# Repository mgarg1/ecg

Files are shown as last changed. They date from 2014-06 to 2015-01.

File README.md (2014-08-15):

ECG
===

An electrocardiograph prototype for the Remote Neonatal Monitoring and Intervention Project.

Dependencies
------------

- Python 2.7
- Arduino >= 1.5.6-r2 (for Arduino Due)
- stream-plot (source included, but streamplot's dependencies need to be met) - https://github.com/s-gv/stream-plot
- MATLAB / Octave if you want to run simulations
- TI SmartRF Flash Programmer
- IAR 8051 >= 8.30 (only if you want to re-compile the source code for CC2540)
- TI CCDebugger (for programming CC2540)

How-to-use
----------

Wired ECG with Arduino:

- Build the circuit in `schematics/ecg_arduino.png`. A USB to UART converter such as FT232 or CP2102 may be used.
- Program the Arduino with the source in `ecg_arduino/ecg_arduino.ino`.
- Goto `ecg_visualizer_arduino_PC/` and run `python visualizer.py`. If the serial port name is incorrect, edit `visualizer.py`.
- Press the hi-z electrodes across the heart and press the RLD electrode to the leg or forehead. Alternatively, the outer ring of one of the hi-z electrodes can be connected to the RLD electrode. For more details, see the technical report in `report/ecg_tech_report.pdf`. You should now see an ECG signal on the PC display.
- Note that a laptop (with the power cord removed) must be used to power the Arduino. Preferably, keep the laptop on your lap. Interference will be much worse if a mains powered desktop is used; the interference may be so strong as to saturate the amplifiers leading to no useful ECG signal at all.

Wireless ECG with Bluetooth Low Energy (BLE using CC2540):

- Build the circuit in `schematics/ecg_CC2540.png`. A more complete schematic is in `schematics/ecg_CC2540_full.png`. Program the CC2540 in the circuit with the hex file `ecg_CC2540/hexfiles/SimpleBLEPeripheral.hex`.
- Connect the CC2540 USB dongle to a PC (either a laptop or a mains powered desktop will do). Program the CC2540 USB dongle with the hex file `ecg_CC2540/hexfiles/CC2540_USBdongle_HostTestRelease_All.hex`.
- Goto `ecg_visualizer_ble_PC/` and run `python visualizer.py`. If the serial port name is incorrect, edit `visualizer.py`.
- Press the hi-z electrodes across the heart and press the RLD electrode to the leg or forehead. Alternatively, the outer ring of one of the hi-z electrodes can be connected to the RLD electrode. For more details, see the technical report in `report/ecg_tech_report.pdf`. You should now see an ECG signal on the PC display. A sample recording may be found [here](https://github.com/s-gv/ecg/blob/master/data/ble_single_battery_LP5907_psuedo2_RLD/screenshots/screenshot0.png).
- Note that the CC2540, which is gathering ECG data and transmitting wirelessly, has to be powered by a battery (ex: CR2032 coin cell). If a mains power source is used, interference will be much worse.

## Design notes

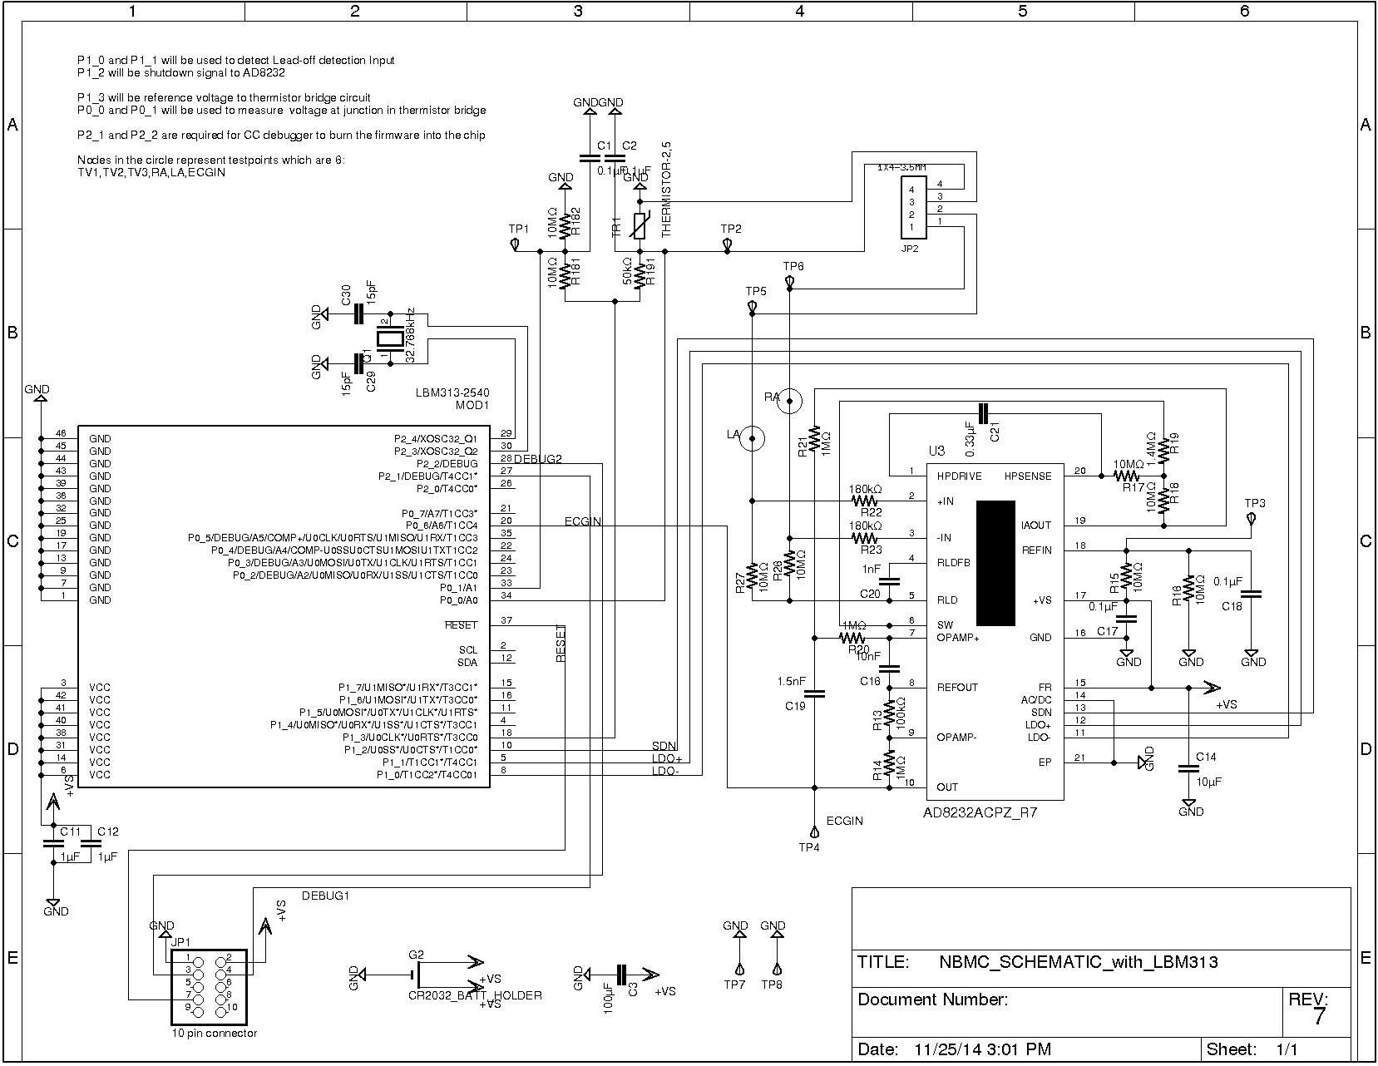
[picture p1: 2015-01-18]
ecg_schematic/LBM313/schematic_black.png

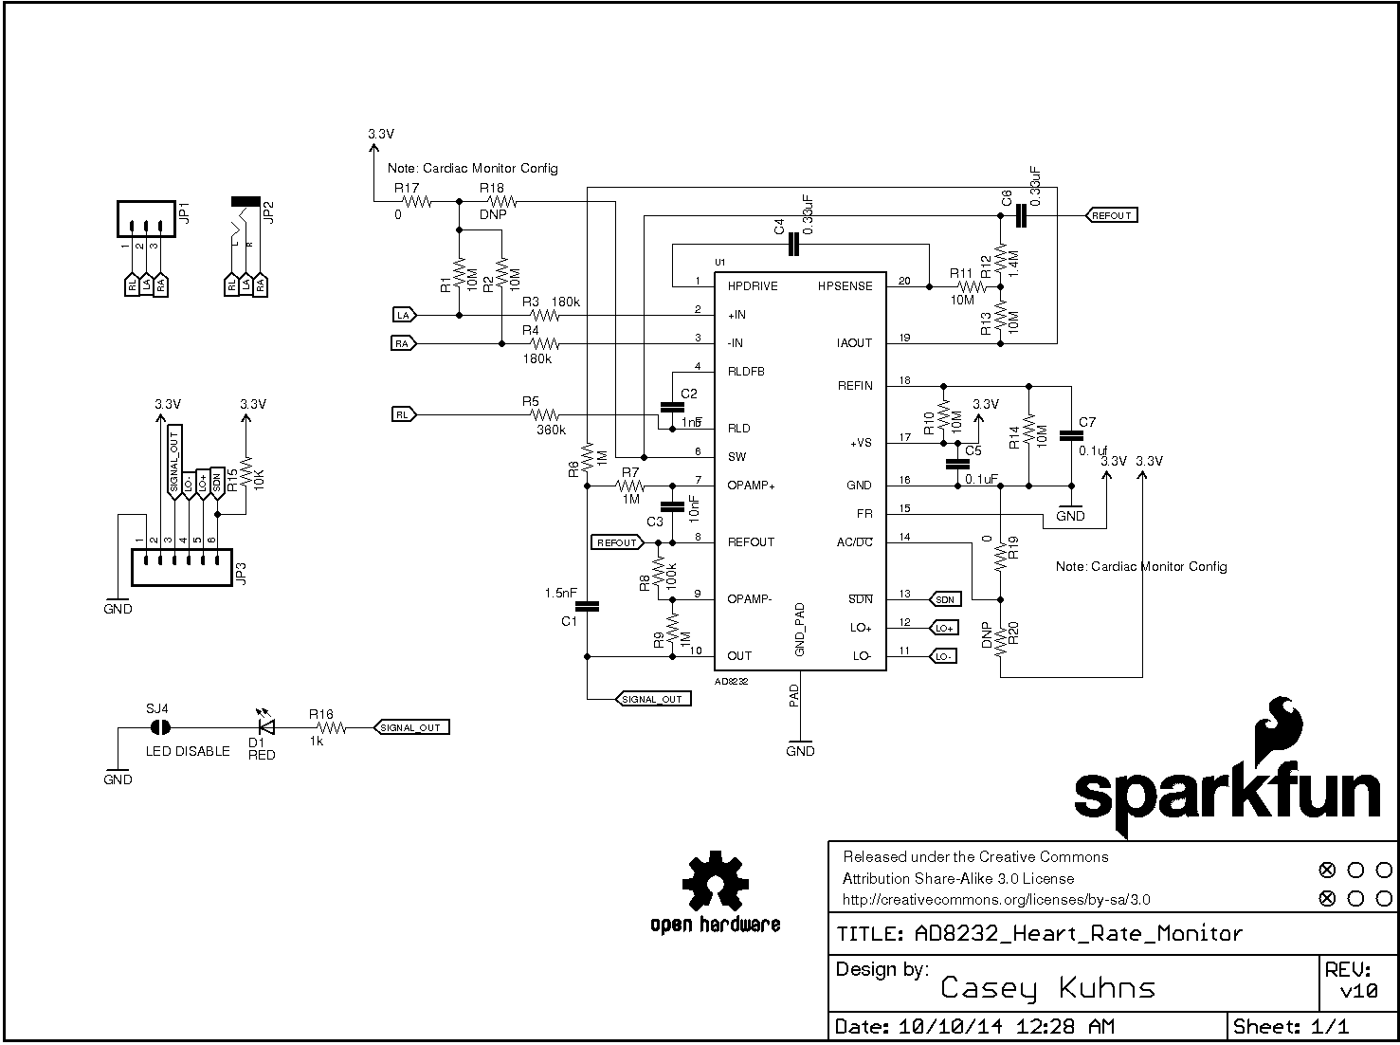
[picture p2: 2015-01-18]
ecg_schematic/Sparkfun_8232/sparkfun_schematic.png

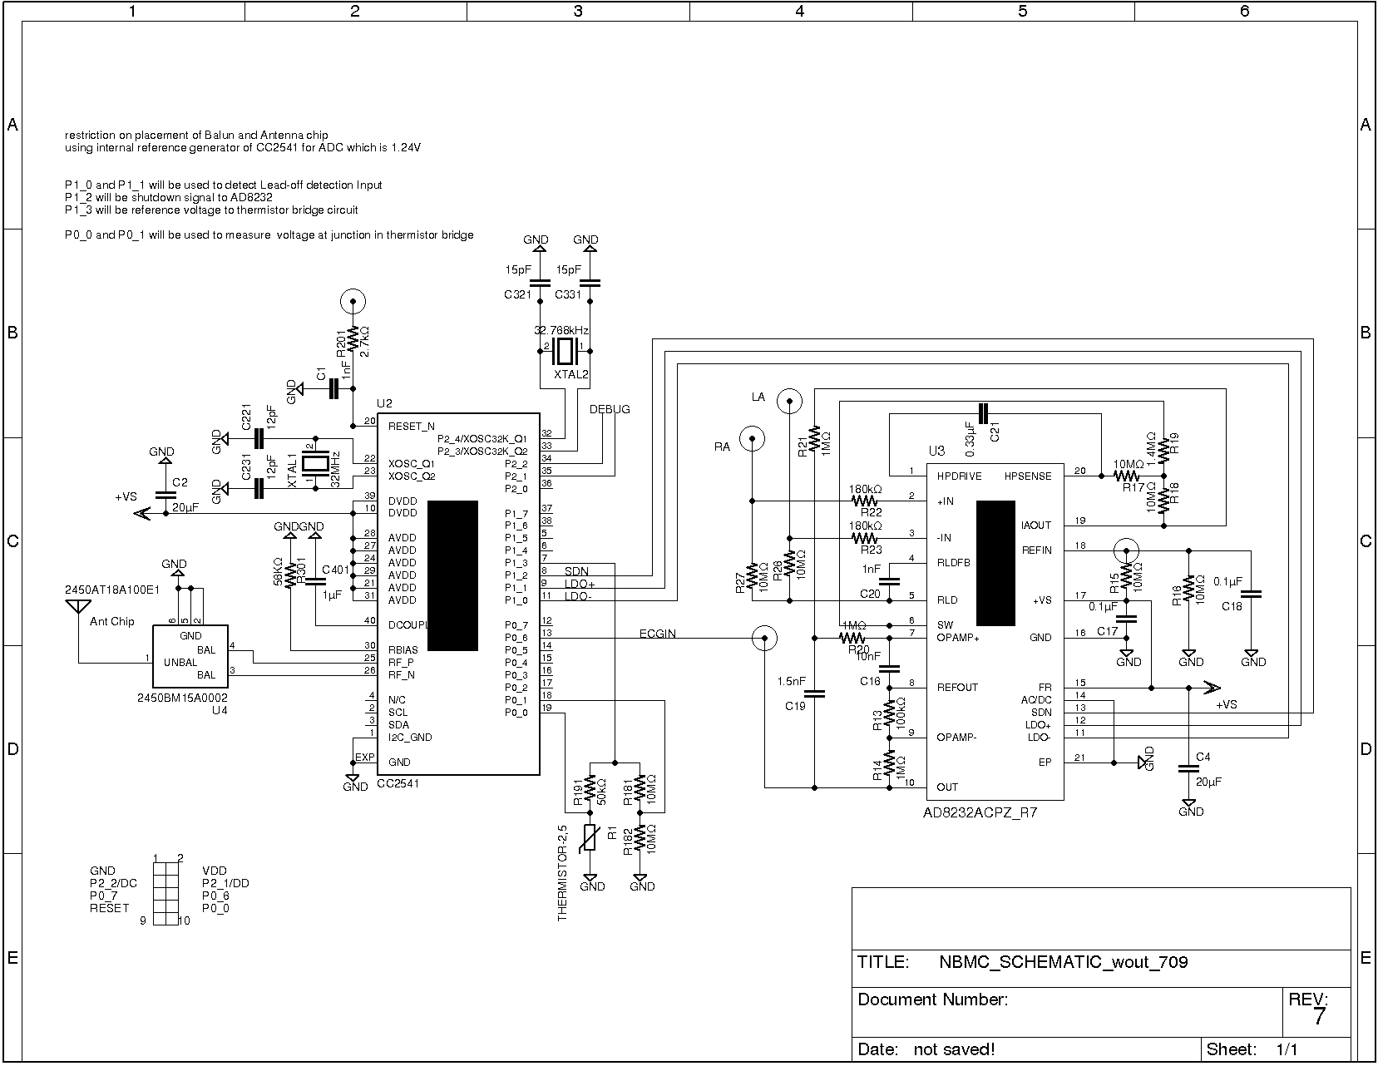
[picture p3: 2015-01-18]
ecg_schematic/NBMC_balun_chip/NBMC_schematic_8.png

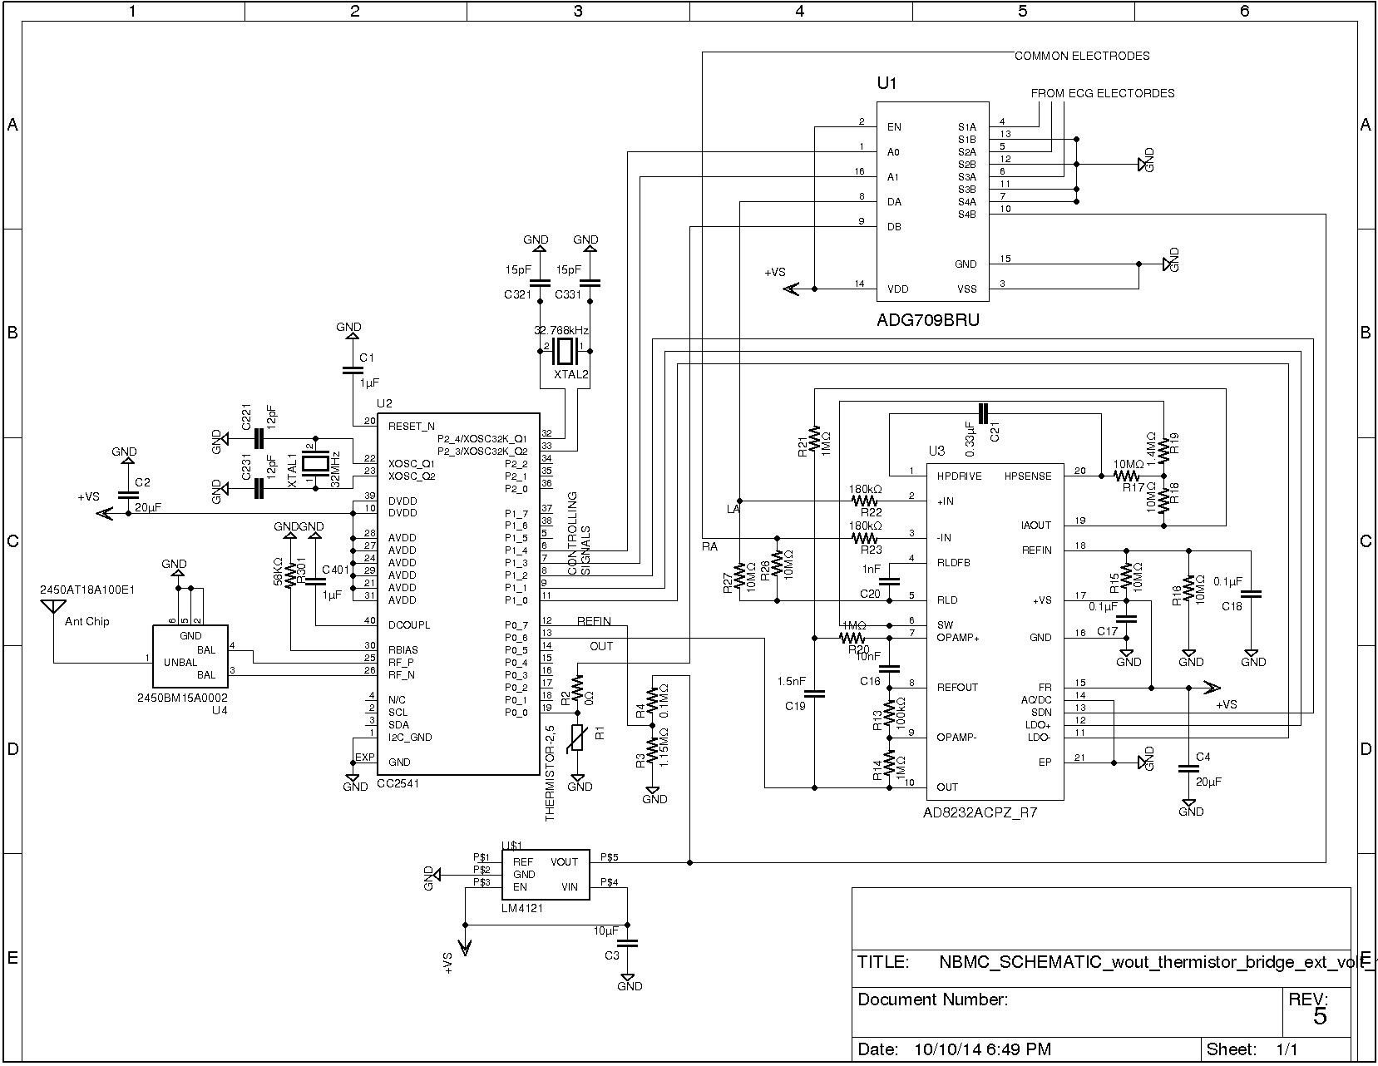
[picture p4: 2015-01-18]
ecg_schematic/NBMC_balun_chip/NBMC_Schematic_5.png

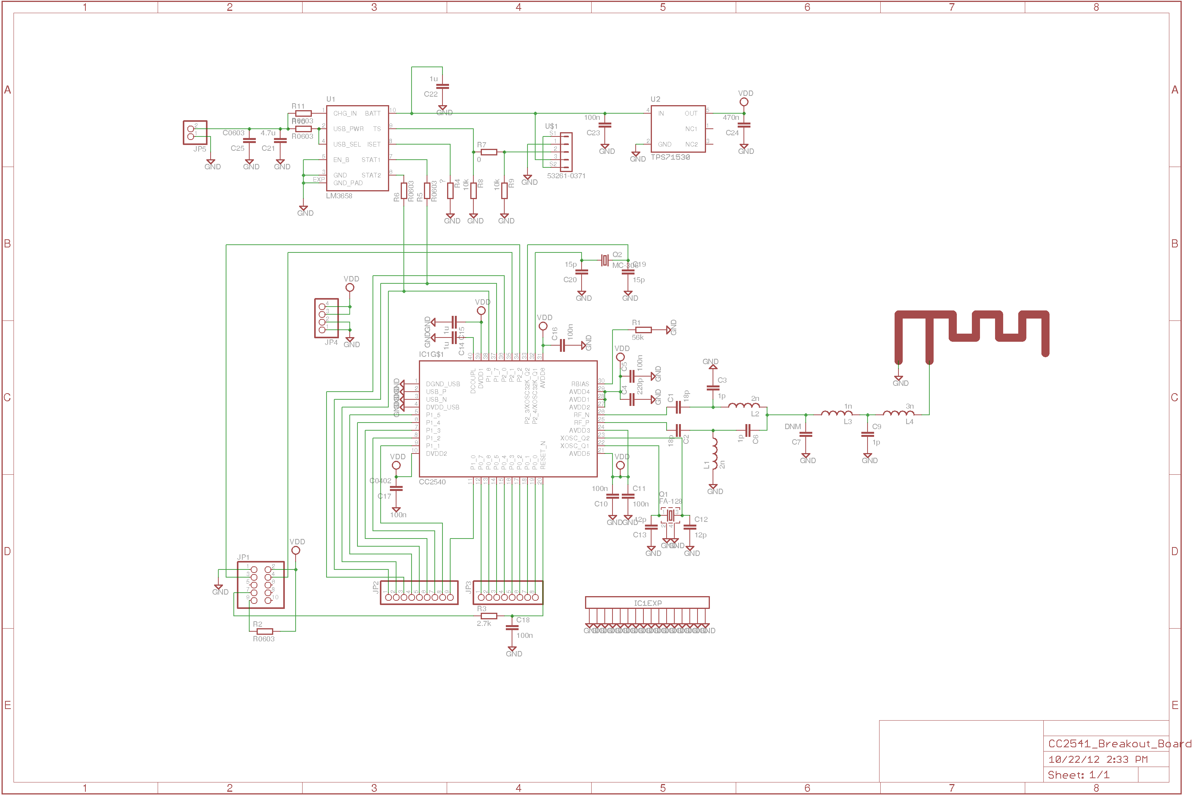
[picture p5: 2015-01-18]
ecg_schematic/CC2541_Breakout_Board_Eagle_files/CC2541_breakout.png

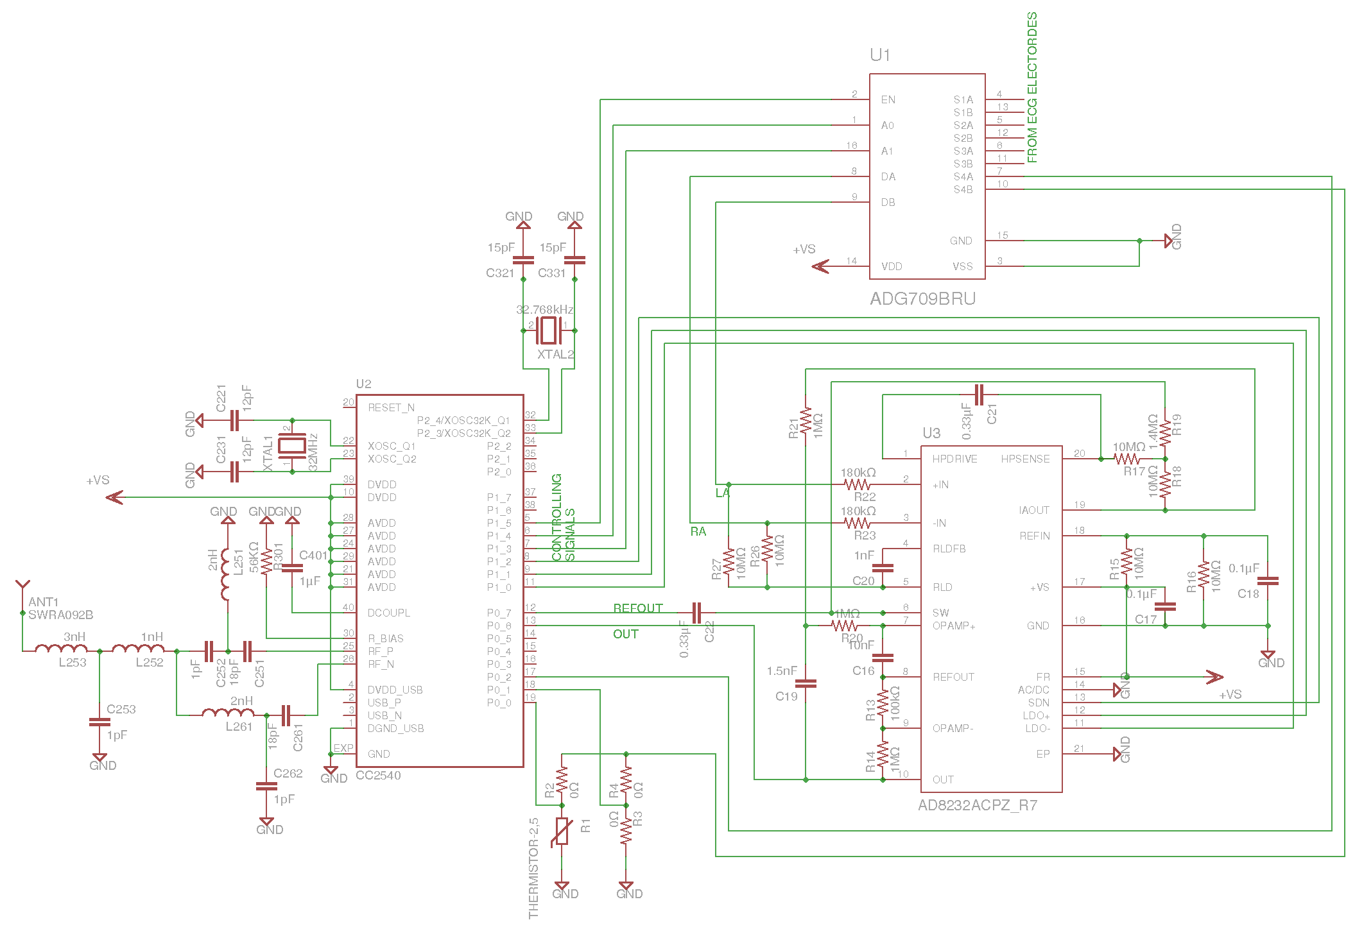
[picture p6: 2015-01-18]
ecg_schematic/NBMC/schematic_thermistor_300.png

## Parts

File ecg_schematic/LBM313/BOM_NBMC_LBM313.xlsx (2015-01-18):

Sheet: Mouser_Only_2
NBMC health Monitor Part List (12/1/2014) |  |  |  |  |  | Kit Count : | 40
Sch. Ref | Package (in) | Description | Pcs/Kit | T.Pcs | Manufacturer | Manufacturer PN | Seller | Seller Part number | Notes
C17,C18,C181,C191 | 402 | 0.1uF capacitor | 4 | 160 | Murata | GRM155R71C104KA88D | Mouser | 81-GRM155R71C104KA88D | Multilayer Ceramic Capacitors MLCC - SMD/SMT 0402 0.1uF 16volts X7R 10%
C21 | 805 | 0.33uF capacitor | 1 | 40 | TDK | C1005X6S0J334M050BC | Mouser | 810-C1005X6S0J334M0C | Multilayer Ceramic Capacitors MLCC - SMD/SMT 0402 0.33uF 6.3volts X6S 20% T=0.5mm
R19 | 402 | 1.4Mohm resistor | 1 | 40 | Vishay Dale | CRCW04021M40FKED | Mouser | 71-CRCW0402-1.4M-E3 | Thick Film Resistors - SMD 1/16watt 1.4Mohms 1%
C19 | 402 | 1.5nF capacitor | 1 | 40 | Murata | GRM155R71H152KA01D | Mouser | 81-GRM155R71H152KA01D | Multilayer Ceramic Capacitors MLCC - SMD/SMT 0402 1500pF 50volts X7R 10%
JP1 | SMT 0.050" spacing | 10 pin connector | 1 | 40 | FCI | 20021121-00010C4LF | Mouser | 649-202112100010C4LF | Headers & Wire Housings 10P HDR UNSHRD 1.27x1.27MM BTB SMT
R13 | 402 | 100kohm resistor | 1 | 40 | Panasonic | ERJ-2RKF1003X | Mouser | 667-ERJ-2RKF1003X | Thick Film Resistors - SMD 0402 100Kohms 1% Tol
C3 | 1210 | 100uF capacitor | 1 | 40 | AVX | TAJB107M006RNJ | Mouser | 581-TAJB107M006R | Tantalum Capacitors - Solid SMD 6.3volts 100uF 20%
R15,R16,R17,R18,R26,R27 | 402 | 10Mohm resistor | 6 | 240 | KOA | RK73H1ETTP1005F | Mouser | 660-RK73H1ETTP1005F | Thick Film Resistors - SMD 10M OHM 1%
C16 | 402 | 10nF capacitor | 1 | 40 | Murata | GRM155R71E103KA01D | Mouser | 81-GRM155R71E103KA01D | Multilayer Ceramic Capacitors MLCC - SMD/SMT 0402 0.01uF 25volts X7R 10%
C14 | 402 | 10uF capacitor | 1 | 40 | Murata | GRM155R60J106ME44D | Mouser | 81-GRM155R60J106ME44D | Multilayer Ceramic Capacitors MLCC - SMD/SMT 10UF 6.3V 20% 0402
C29,C30 | 402 | 15pF capacitor | 2 | 80 | AVX | 04023A150KAT2A | Mouser | 581-04023A150KAT2A | Multilayer Ceramic Capacitors MLCC - SMD/SMT 25volts 15pF 10% C0G
R22,R23 | 402 | 180kohm resistor | 2 | 80 | Panasonic | ERJ-2RKF1803X | Mouser | 667-ERJ-2RKF1803X | Thick Film Resistors - SMD 0402 180Kohms 1% Tol
R14,R20,R21 | 402 | 1Mohm resistor | 3 | 120 | Panasonic | ERJ-2RKF1004X | Mouser | 667-ERJ-2RKF1004X | Thick Film Resistors - SMD 0402 1Mohms 1% Tol
C20,C32 | 402 | 1nF capacitor | 2 | 80 | Murata | GRM1555C1H102JA01D | Mouser | 81-GRM1555C1H102JA01D | Multilayer Ceramic Capacitors MLCC - SMD/SMT 0402 1000pF 50volts C0G 5%
C11,C12 | 402 | 1uF capacitor | 2 | 80 | Murata | GRM155R61A105KE15D | Mouser | 81-GRM155R61A105KE15 | Multilayer Ceramic Capacitors MLCC - SMD/SMT 0402 1uF 10volts X5R 10%
Q1 | 2x1.2mm | 32.768kHz Crystal | 1 | 40 | ECS | ECS-.327-12.5-12-TR | Mouser | 520-ECS-.327-12.5-12-TR | Crystals 32.768KHz 12.5pF 20ppm -40C +85C
R181,R182 | 402 | 330Kohm resistor | 2 | 80 | Vishay Dale | CRCW0402330KFKED | Mouser | 71-CRCW0402330KFKED | Thick Film Resistors - SMD 1/16watt 330Kohms 1%
R28 | 402 | 4.7Kohm resistor | 1 | 40 | Panasonic | ERJ-2RKF4701X | Mouser | 667-ERJ-2RKF4701X | Thick Film Resistors - SMD 0402 4.7Kohms 1% Tol
R191 | 402 | 50Kohm resistor | 1 | 40 | Vishay Dale | CRCW040250K0FKED | Mouser | 71-CRCW040250K0FKED | To be bought
U3 | CSP-20 (4x4mm) | Analog ECG Front End | 1 | 40 | Analog Devices | AD8232ACPZ-R7 | Mouser | 584-AD8232ACPZ-R7 | Instrumentation Amplifiers SGL-Lead Heart Rate Monitor
G1 | 20mm dia | Coin-Cell Battery | 1 | 40 | Panasonic | CR2032 | Mouser | 658-CR2032 | Coin Cell Battery 3V 20X3.2MM 225mAH
MOD1 | 16X 12mm | BLE Module with Antenna | 1 | 40 | Punch Through Design | LBM313-2540-256 | Xpunch Through Design | LBM313-2540-256
JP2 |  | 4 pin connector | 1 | 40 |  |  | XX |  | Not to be purchased - Connect to Berkley Sensor
G2 | NA | Battery Holder | 1 | 40 | Philmore | BH2040 | XX |  | Already purchased – Attached with double sided tape, pins soldered to flex tab
TP1-8 | NA | Test Points | 8 | 320 | NA | NA | XXNA | NA | Not to be purchased
TR1 | See Gerber Data |  | 1 | 40 | NA | NA | XXBerk | NA | Berkley printed sensor; one thermister on bottom side
ECG sensor | See Gerber Data |  | 1 | 40 |  |  | XXBerk |  | Berkley printed sensor two gold electrodes on bottom side
 |  |  | 49 | 1960

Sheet: Original
NBMC health Monitor Part List (12/1/2014) |  |  |  |  |  |  | Kit Count : | 40
Sch. Ref | Package (in) | Description | Part name | Pcs/Kit | T.Pcs | Manufacturer | Manufacturer PN | Seller | Seller Part number | Notes
C17,C18,C181,C191 | 402 | 0.1uF capacitor | C_0.1uF_0402 | 4 | 160 | Murata | GRM155R71C104KA88D | Mouser | 81-GRM155R71C104KA88D
C21 | 805 | 0.33uF capacitor | C_0.33uF_0805 | 1 | 40 | Murata | GRM319R71H334KA01D | Mouser | 81-TAJB107M006RNJ
R19 | 402 | 1.4Mohm resistor | R_1.4M_0402_F | 1 | 40 | Vishay Dale | CRCW04021M40FKED | Mouser | 71-CRCW0402-1.4M-E3
C19 | 402 | 1.5nF capacitor | C_1.5nF_0402 | 1 | 40 | Murata | GRM155R71H152KA01D | Mouser | 81-20021121-00010C4LF
JP1 | SMT 0.050" spacing | 10 pin connector |  | 1 | 40 | FCI | 20021121-00010C4LF | Digikey |  | For debug; available at Digikey
R13 | 402 | 100kohm resistor | R_100K_0402_F | 1 | 0 | Yageo | RC0402FR-07100KL | Digikey
C3 | 1210 | 100uF capacitor | C_100uF_1210 | 1 | 40 | AVX | TAJB107M006RNJ | Mouser | 581-TAJB107M006R | Capacitor, 100uF, 0402, 20%, 6.3V
R15,R16,R17,R18,R26,R27 | 402 | 10Mohm resistor | R_10M_0402_F | 6 | 240 | KOA | RK73H1ETTP1005F | Mouser | 660-RK73H1ETTP1005F
C16 | 402 | 10nF capacitor | C_10nF_0402 | 1 | 40 | Murata | GRM155R71E103KA01D | Mouser | 81-CRCW04021M40FKED
C14 | 402 | 10uF capacitor | C_10uF_0402 | 1 | 40 | Murata | GRM155R60J106ME44D | Mouser | 81-GRM319R71H334KA01D
C29,C30 | 402 | 15pF capacitor | C_15P_0402 | 2 | 80 | Murata | GRM1555C1H150JZ01D | Digikey |  | Capacitor, 15p, 0402, NP0, 5%, 50V
R22,R23 | 402 | 180kohm resistor | R_180K_0402_F | 2 | 80 | Yageo | RC0402FR-07180KL | Digikey
R14,R20,R21 | 402 | 1Mohm resistor | R_1M_0402_F | 3 | 120 | Yageo | RC0402FR-071ML | Digikey
C20,C32 | 402 | 1nF capacitor | C_1nF_0402 | 2 | 80 | Murata | GRM1555C1H102JA01D | Mouser | 81-RC0402FR-07100KL
C11,C12 | 402 | 1uF capacitor | C_1uF_0402 | 2 | 80 | Murata | GRM155R61A105KE15D | Mouser | 81-GRM155R61A105KE15
Q1 | 2x1.2mm | 32.768kHz Crystal | X_32.768/20/50/40/12 | 1 | 40 | ECS | ECS-.327-12.5-12-TR | Mouser | 520-ECS-.327-12.5-12-TR | Crystal, 32.768 kHz, 12.5pF, 20/50 ppm,SMD package
R181,R182 | 402 | 330Kohm resistor | R_330K_0402_F | 2 | 80 | Yageo | RC0402FR-07330KL | Digikey
JP2 |  | 4 pin connector |  | 1 | 40 |  |  | NA |  | Not to be purchased - Connect to Berkley Sensor
R28 | 402 | 4.7Kohm resistor | R_4.7K_0402_F | 1 | 40 | Panasonic | ERJ-2RKF4701X | Mouser | 667-ERJ-2RKF4701X | Filter Component
R191 | 402 | 50Kohm resistor | Themistor – Resistor | 1 | 40 | Vishay Dale | CRCW040250K0FKED | Mouser | 71-CRCW040250K0FKED | High Tolerance Resistor
U3 | CSP-20 (4x4mm) | Analog ECG Front End | AD8232 | 1 | 40 | Analog Devices | AD8232ACPZ-R7 | Mouser | 584-AD8232ACPZ-R7
G2 | NA | Battery Holder |  | 1 | 40 | Philmore | BH2040 |  |  | Already purchased – Attached with double sided tape, pins soldered to flex tab
MOD1 | 16X 12mm | BLE Module with Antenna | LBM313-2540 | 1 | 40 | Punch Through Design | LBM313-2540-256 | Punch Through Design | LBM313-2540-256
G1 | 20mm dia | Coin-Cell Battery | CR2032 | 1 | 40 | Panasonic | CR2032 | Mouser | 658-CR2032
TP1-8 | NA | Test Points | TP09R | 8 | 320 | NA | NA | NA | NA | Not to be purchased
TR1 | See Gerber Data |  | Themistor | 1 | 40 | TBD | TBD | TBD | TBD | Berkley printed sensor; one thermister on bottom side
ECG sensor | See Gerber Data |  |  | 1 | 40 |  |  |  |  | Berkley printed sensor two gold electrodes on bottom side
 |  |  | Total : | 49 | 1960

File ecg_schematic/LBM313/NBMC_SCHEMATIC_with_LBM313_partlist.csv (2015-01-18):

Qty | Value | Device | Package | Parts | Description | TP_SIGNAL_NAME
4 | 0.1µF | C-EUC0402 | C0402 | C17, C18, C181, C191 | CAPACITOR, European symbol
1 | 0.33µF | C-EUC0402 | C0402 | C21 | CAPACITOR, European symbol
1 | 1.4MΩ | R-US_R0402 | R0402 | R19 | RESISTOR, American symbol
1 | 1.5nF | C-EUC0402 | C0402 | C19 | CAPACITOR, European symbol
1 | 10 pin connector | PINHD-2X5 | 2X05 | JP1 | PIN HEADER
1 | 100kΩ | R-US_R0402 | R0402 | R13 | RESISTOR, American symbol
1 | 100µF | C-EUC0402 | C0402 | C3 | CAPACITOR, European symbol
8 | 10MΩ | R-US_R0402 | R0402 | R15, R16, R17, R18, R26, R27, R181, R182 | RESISTOR, American symbol
1 | 10nF | C-EUC0402 | C0402 | C16 | CAPACITOR, European symbol
1 | 10µF | C-EUC0402 | C0402 | C14 | CAPACITOR, European symbol
2 | 15pF | C-EUC0402 | C0402 | C291, C301 | CAPACITOR, European symbol
2 | 180kΩ | R-US_R0402 | R0402 | R22, R23 | RESISTOR, American symbol
2 | 1MΩ | R-US_R0402 | R0402 | R14, R21 | RESISTOR, American symbol
1 | 1MΩ | R-US_R0402 | R0402 | R20 | RESISTOR, American symbol
1 | 1X4-3.5MM | 1X4-3.5MM | 1X04-3.5MM | JP2 | 4-pin connector
1 | 1nF | C-EUC0402 | C0402 | C20 | CAPACITOR, European symbol
2 | 1µF | C-EUC0402 | C0402 | C11, C12 | CAPACITOR, European symbol
1 | 32.768kHz | XTAL | Q | Q1 | CRYSTAL
1 | 50kΩ | R-US_R0402 | R0402 | R191 | RESISTOR, American symbol
1 | AD8232ACPZ_R7 | AD8232ACPZ_R7 | CP_20_10 | U3
1 | CR2032_BATT_HOLDER | CR2032SMT | CR2032-SMD | G2
1 | LBM313-2540 | LBM313-2540 | LBM313-2540 | MOD1 | Bluetooth 4.0 Module. Documentation at: http://punchthrough.com/docs/doku.php?id=lbm313
1 | THERMISTOR-2,5 | THERMISTOR-2,5 | RS-2,5 | TR1 | THERMISTOR
8 | TPSTP09R | TPSTP09R | TP09R | TP1, TP2, TP3, TP4, TP5, TP6, TP7, TP8 | TEST PIN

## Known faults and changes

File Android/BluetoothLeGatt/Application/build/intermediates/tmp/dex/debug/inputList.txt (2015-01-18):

C:\Users\mohit\Desktop\NBMC_Project\ecg\Android\BluetoothLeGatt\Application\build\intermediates\classes\debug
C:\Users\mohit\Desktop\NBMC_Project\ecg\Android\BluetoothLeGatt\Application\build\intermediates\pre-dexed\debug\internal_impl-21.0.2-8ebbc263ad53806d63095860c9af35b756f6e820.jar
C:\Users\mohit\Desktop\NBMC_Project\ecg\Android\BluetoothLeGatt\Application\build\intermediates\pre-dexed\debug\support-annotations-21.0.2-b8752aa791ef7f693920b21538d24f9baba78135.jar
C:\Users\mohit\Desktop\NBMC_Project\ecg\Android\BluetoothLeGatt\Application\build\intermediates\pre-dexed\debug\classes-3411cea97a7a49cd5b14c5f6cc2da01509a3eb8a.jar
C:\Users\mohit\Desktop\NBMC_Project\ecg\Android\BluetoothLeGatt\Application\build\intermediates\pre-dexed\debug\classes-53aedaaf6633a4929487d5a55c5920723a60678f.jar
C:\Users\mohit\Desktop\NBMC_Project\ecg\Android\BluetoothLeGatt\Application\build\intermediates\pre-dexed\debug\internal_impl-21.0.2-81f189868740bda604251d7c963f9b130662219a.jar
C:\Users\mohit\Desktop\NBMC_Project\ecg\Android\BluetoothLeGatt\Application\build\intermediates\pre-dexed\debug\classes-7fd10a7327951d70120f01703a9f8243db2020d3.jar

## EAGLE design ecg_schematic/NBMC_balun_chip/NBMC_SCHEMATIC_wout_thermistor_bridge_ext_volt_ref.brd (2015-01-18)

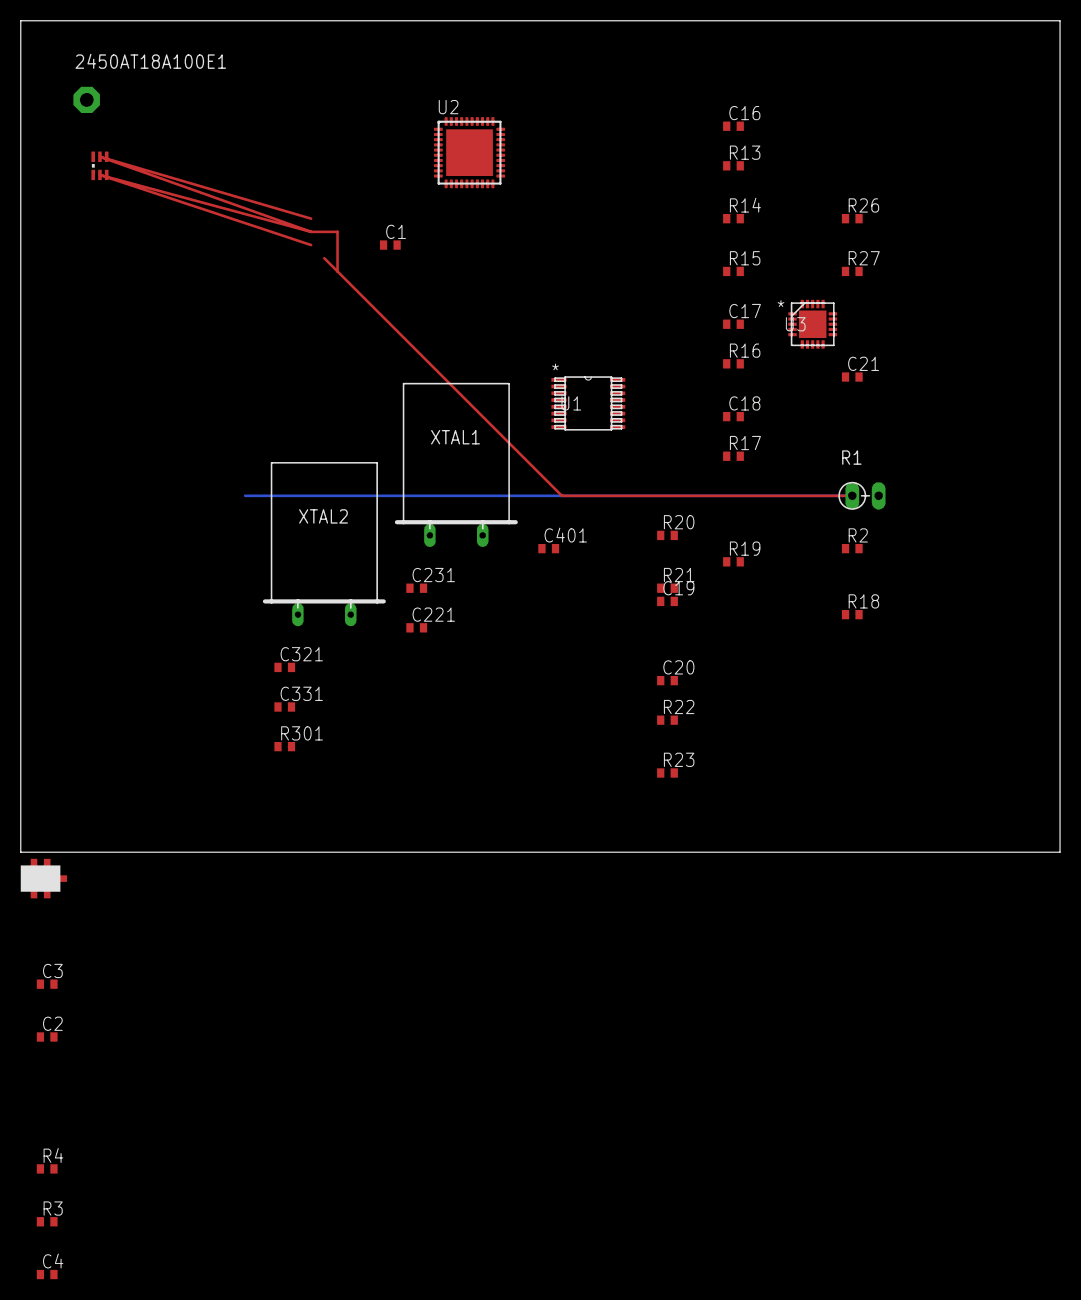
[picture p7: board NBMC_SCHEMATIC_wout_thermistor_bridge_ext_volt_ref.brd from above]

Board: 2 copper layers, 100.0 x 80.0 mm, 41 parts (0 on the bottom side), 38 nets.

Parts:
2450AT18A100E1: Ant Chip; PAD-01
C1, C401: 1µF; C0402
C2, C4: 20µF; C0402
C3: 10µF; C0402
C16: 10nF; C0402
C17, C18: 0.1µF; C0402
C19: 1.5nF; C0402
C20: 1nF; C0402
C21: 0.33µF; C0402
C221, C231: 12pF; C0402
C321, C331: 15pF; C0402
R1: THERMISTOR-2,5; RS-2,5
R2: 0Ω; R0402
R3: 1.15MΩ; R0402
R4: 0.1MΩ; R0402
R13: 100kΩ; R0402
R14, R20, R21: 1MΩ; R0402
R15, R16, R17, R18, R26, R27: 10MΩ; R0402
R19: 1.4MΩ; R0402
R22, R23: 180kΩ; R0402
R301: 56KΩ; R0402
U1: ADG709BRU; RU_16
U2: CC2541; RHA_S-PVQFN-N40
U3: AD8232ACPZ_R7; CP_20_10
U4: 2450BM15A0002
U$1: LM4121; 0402
XTAL1: 32MHz; Q
XTAL2: 32.768kHz; Q

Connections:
GND: C1.1, C2.1, C3.1, C4.2, C17.1, C18.1, C221.1, C231.1, C321.2, C331.2, C401.1, R1.1, R3.1, R16.1, R301.1, U1.3, U1.11, U1.12, U1.13, U1.15, U2.1, U2.EXP, U3.14, U3.16, U3.21, U4.2, U4.5, U4.6, U$1.P$2
unnamed: U2.26, U4.3
unnamed: R301.2, U2.30
unnamed: C1.2, U2.20
unnamed: U2.25, U4.4
unnamed: R4.2, U$1.P$5
unnamed: 2450AT18A100E1.1, U4.1
unnamed: C401.2, U2.40
unnamed: R2.2, U1.9
unnamed: R1.2, R2.1, U2.19
unnamed: C221.2, U2.22, XTAL1.2
unnamed: C231.2, U2.23, XTAL1.1
unnamed: C321.1, U2.32, XTAL2.2
unnamed: C331.1, U2.33, XTAL2.1
unnamed: R22.1, U3.2
unnamed: R3.2, R4.1, U2.12
unnamed: C20.1, R26.1, R27.1, U3.5
unnamed: U1.1, U2.6
unnamed: U1.16, U2.7
unnamed: R23.1, U3.3
unnamed: R19.1, U3.6
unnamed: U2.11, U3.11
unnamed: U2.9, U3.12
unnamed: U2.8, U3.13
unnamed: C19.2, R20.2, R21.1
unnamed: R22.2, R27.2
unnamed: R13.1, R14.2, U3.9
unnamed: R23.2, R26.2
unnamed: C16.2, R20.1, U3.7
unnamed: C16.1, R13.2, U3.8
unnamed: C19.1, R14.1, U2.13, U3.10
unnamed: C18.2, R15.2, R16.2, U3.18
unnamed: R18.2, R21.2, U3.19
unnamed: C21.1, R17.2, U3.20
unnamed: R17.1, R18.1, R19.2
unnamed: C20.2, U3.4
unnamed: C21.2, U3.1
VSS: C2.2, C3.2, C4.1, C17.2, R15.1, U1.2, U1.14, U2.10, U2.21, U2.24, U2.27, U2.28, U2.29, U2.31, U2.39, U3.15, U3.17, U$1.P$3, U$1.P$4

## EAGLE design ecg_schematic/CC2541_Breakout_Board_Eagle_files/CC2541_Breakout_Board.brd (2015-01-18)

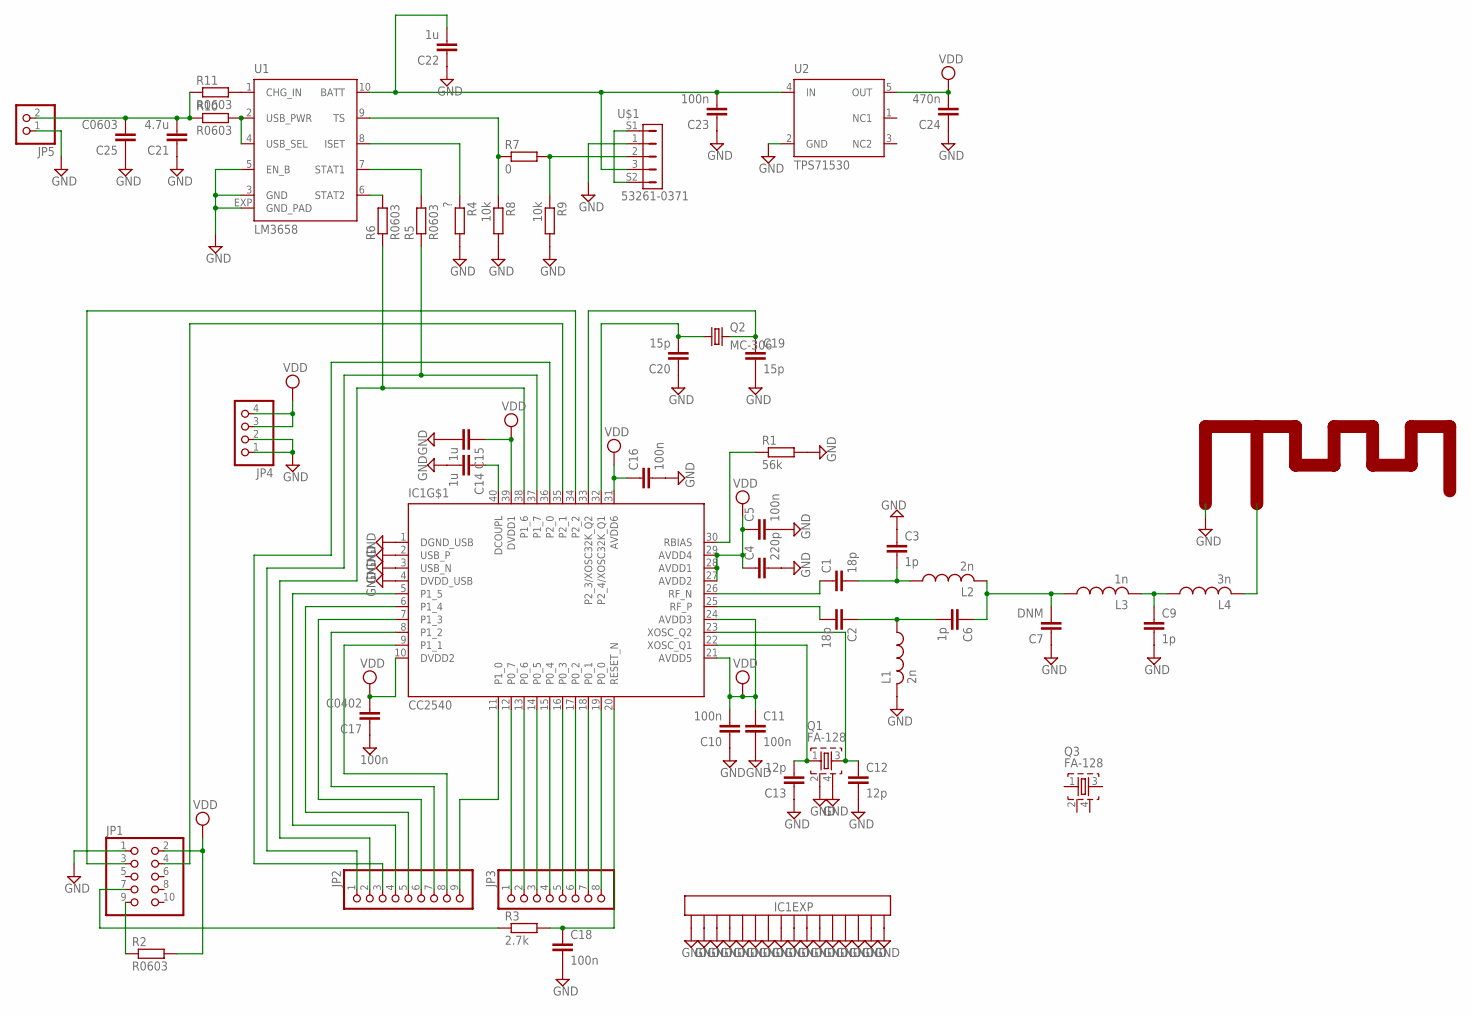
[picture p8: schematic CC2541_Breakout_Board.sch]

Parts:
A1: TI_2.4GHZ_MIFALEFT; TI_2.4GHZ_MIFA_LEFT
C1, C2: 18p; C0402
C3, C6, C9: 1p; C0402
C4: 220p; C0402
C5, C10, C11, C16, C18, C23: 100n; C0402
C7: DNM; C0402
C12, C13: 12p; C0402
C14, C15, C22: 1u; C0402
C17: C0402
C19, C20: 15p; C0402
C21: 4.7u; C0402
C24: 470n; C0402
C25: C0603
IC1: CC2540; QFN40-6X6
JP1: PINHD-2X51.27_SMD; 2X05_1.27_SMD
JP2: PINHD-1X9; 1X09
JP3: PINHD-1X8; 1X08
JP4: PINHD-1X4; 1X04
JP5: PINHD-1X2; 1X02
L1, L2: 2n; C0402
L3: 1n; C0402
L4: 3n; C0402
Q1, Q3: FA-128
Q2: MC-306
R1: 56k; C0402
R2, R5, R6, R10, R11: R0603; C0603
R3: 2.7k; C0402
R4: ?; C0402
R7: 0; C0402
R8, R9: 10k; C0402
U1: LM3658; LLP10
U2: TPS71530; SC70
U$1: 53261-0371; 53261-03

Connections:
CONNECTOR_MOUNT: U$1.S1, U$1.S2
GND: A1.GND, C3.1, C4.2, C5.2, C7.1, C9.2, C10.1, C11.2, C12.2, C13.1, C14.2, C15.2, C16.2, C17.1, C18.2, C19.2, C20.1, C21.1, C22.1, C23.1, C24.1, C25.1, IC1.1 (DGND_USB), IC1.2 (USB_P), IC1.3 (USB_N), IC1.4 (DVDD_USB), IC1.EXP@1 (EXP16), IC1.EXP@2 (EXP16), IC1.EXP@3 (EXP16), IC1.EXP@4 (EXP16), IC1.EXP@5 (EXP16), IC1.EXP@6 (EXP16), IC1.EXP@7 (EXP16), IC1.EXP@8 (EXP16), IC1.EXP@9 (EXP16), IC1.EXP@10 (EXP16), IC1.EXP@11 (EXP16), IC1.EXP@12 (EXP16), IC1.EXP@13 (EXP16), IC1.EXP@14 (EXP16), IC1.EXP@15 (EXP16), IC1.EXP@16 (EXP16), JP1.1, JP4.1, JP4.2, JP5.1, L1.2, Q1.2, Q1.4, R1.2, R4.2, R8.2, R9.2, U1.3 (GND), U1.5 (EN_B), U1.EXP (GND_PAD), U2.2 (GND), U$1.1
unnamed: C1.1, IC1.26 (RF_N)
unnamed: C2.2, IC1.25 (RF_P)
unnamed: C1.2, C3.2, L2.1
unnamed: C2.1, C6.2, L1.1
unnamed: C6.1, C7.2, L2.2, L3.1
unnamed: C9.1, L3.2, L4.1
unnamed: IC1.30 (RBIAS), R1.1
unnamed: C13.2, IC1.22 (XOSC_Q1), Q1.1
unnamed: C12.1, IC1.23 (XOSC_Q2), Q1.3
unnamed: C14.1, IC1.40 (DCOUPL)
unnamed: JP1.7, R3.1
unnamed: JP1.9, R2.1
unnamed: IC1.34 (P2_2), JP1.3
unnamed: IC1.35 (P2_1), JP1.4
unnamed: C18.1, IC1.20 (RESET_N), R3.2
unnamed: C20.2, IC1.32 (P2_4/XOSC32K_Q1), Q2.1
unnamed: C19.1, IC1.33 (P2_3/XOSC32K_Q2), Q2.4 (2)
unnamed: IC1.19 (P0_0), JP3.8
unnamed: IC1.18 (P0_1), JP3.7
unnamed: IC1.17 (P0_2), JP3.6
unnamed: IC1.16 (P0_3), JP3.5
unnamed: IC1.15 (P0_4), JP3.4
unnamed: IC1.14 (P0_5), JP3.3
unnamed: IC1.13 (P0_6), JP3.2
unnamed: IC1.12 (P0_7), JP3.1
unnamed: IC1.11 (P1_0), JP2.9
unnamed: IC1.9 (P1_1), JP2.8
unnamed: IC1.7 (P1_3), JP2.6
unnamed: IC1.8 (P1_2), JP2.7
unnamed: R10.2, U1.2 (USB_PWR), U1.4 (USB_SEL)
unnamed: IC1.6 (P1_4), JP2.5
unnamed: IC1.38 (P1_6), JP2.2, R6.1
unnamed: IC1.37 (P1_7), JP2.1, R5.1
unnamed: R4.1, U1.8 (ISET)
unnamed: C21.2, C25.2, JP5.2, R10.1, R11.1
unnamed: C22.2, C23.2, U1.10 (BATT), U2.4 (IN), U$1.3
unnamed: R5.2, U1.7 (STAT1)
unnamed: R6.2, U1.6 (STAT2)
unnamed: IC1.36 (P2_0), JP2.3
unnamed: R7.2, R9.1, U$1.2
unnamed: R7.1, R8.1, U1.9 (TS)
unnamed: IC1.5 (P1_5), JP2.4
unnamed: R11.2, U1.1 (CHG_IN)
unnamed: A1.FEED, L4.2
NC2: U2.3 (NC2)
VDD: C4.1, C5.1, C10.2, C11.1, C15.1, C16.1, C17.2, C24.2, IC1.10 (DVDD2), IC1.21 (AVDD5), IC1.24 (AVDD3), IC1.27 (AVDD2), IC1.28 (AVDD1), IC1.29 (AVDD4), IC1.31 (AVDD6), IC1.39 (DVDD1), JP1.2, JP4.3, JP4.4, R2.2, U2.5 (OUT)

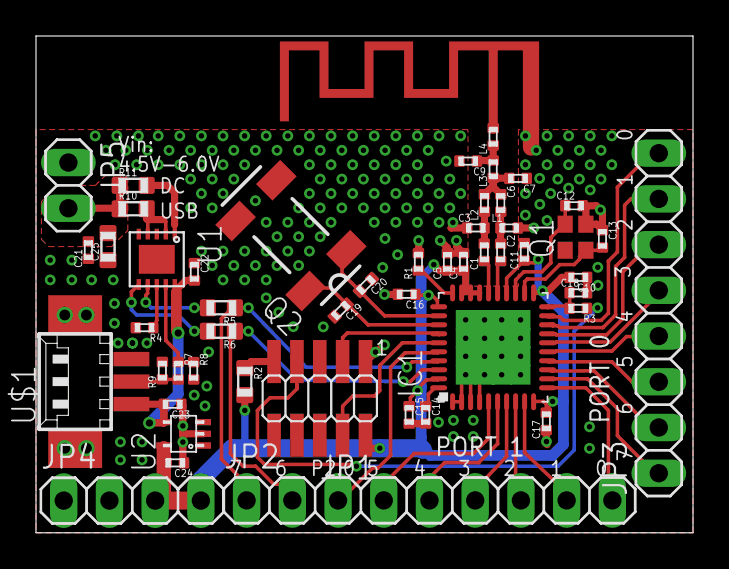
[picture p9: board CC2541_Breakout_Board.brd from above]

Board: 2 copper layers, 36.5 x 27.6 mm, 51 parts (0 on the bottom side), 47 nets.

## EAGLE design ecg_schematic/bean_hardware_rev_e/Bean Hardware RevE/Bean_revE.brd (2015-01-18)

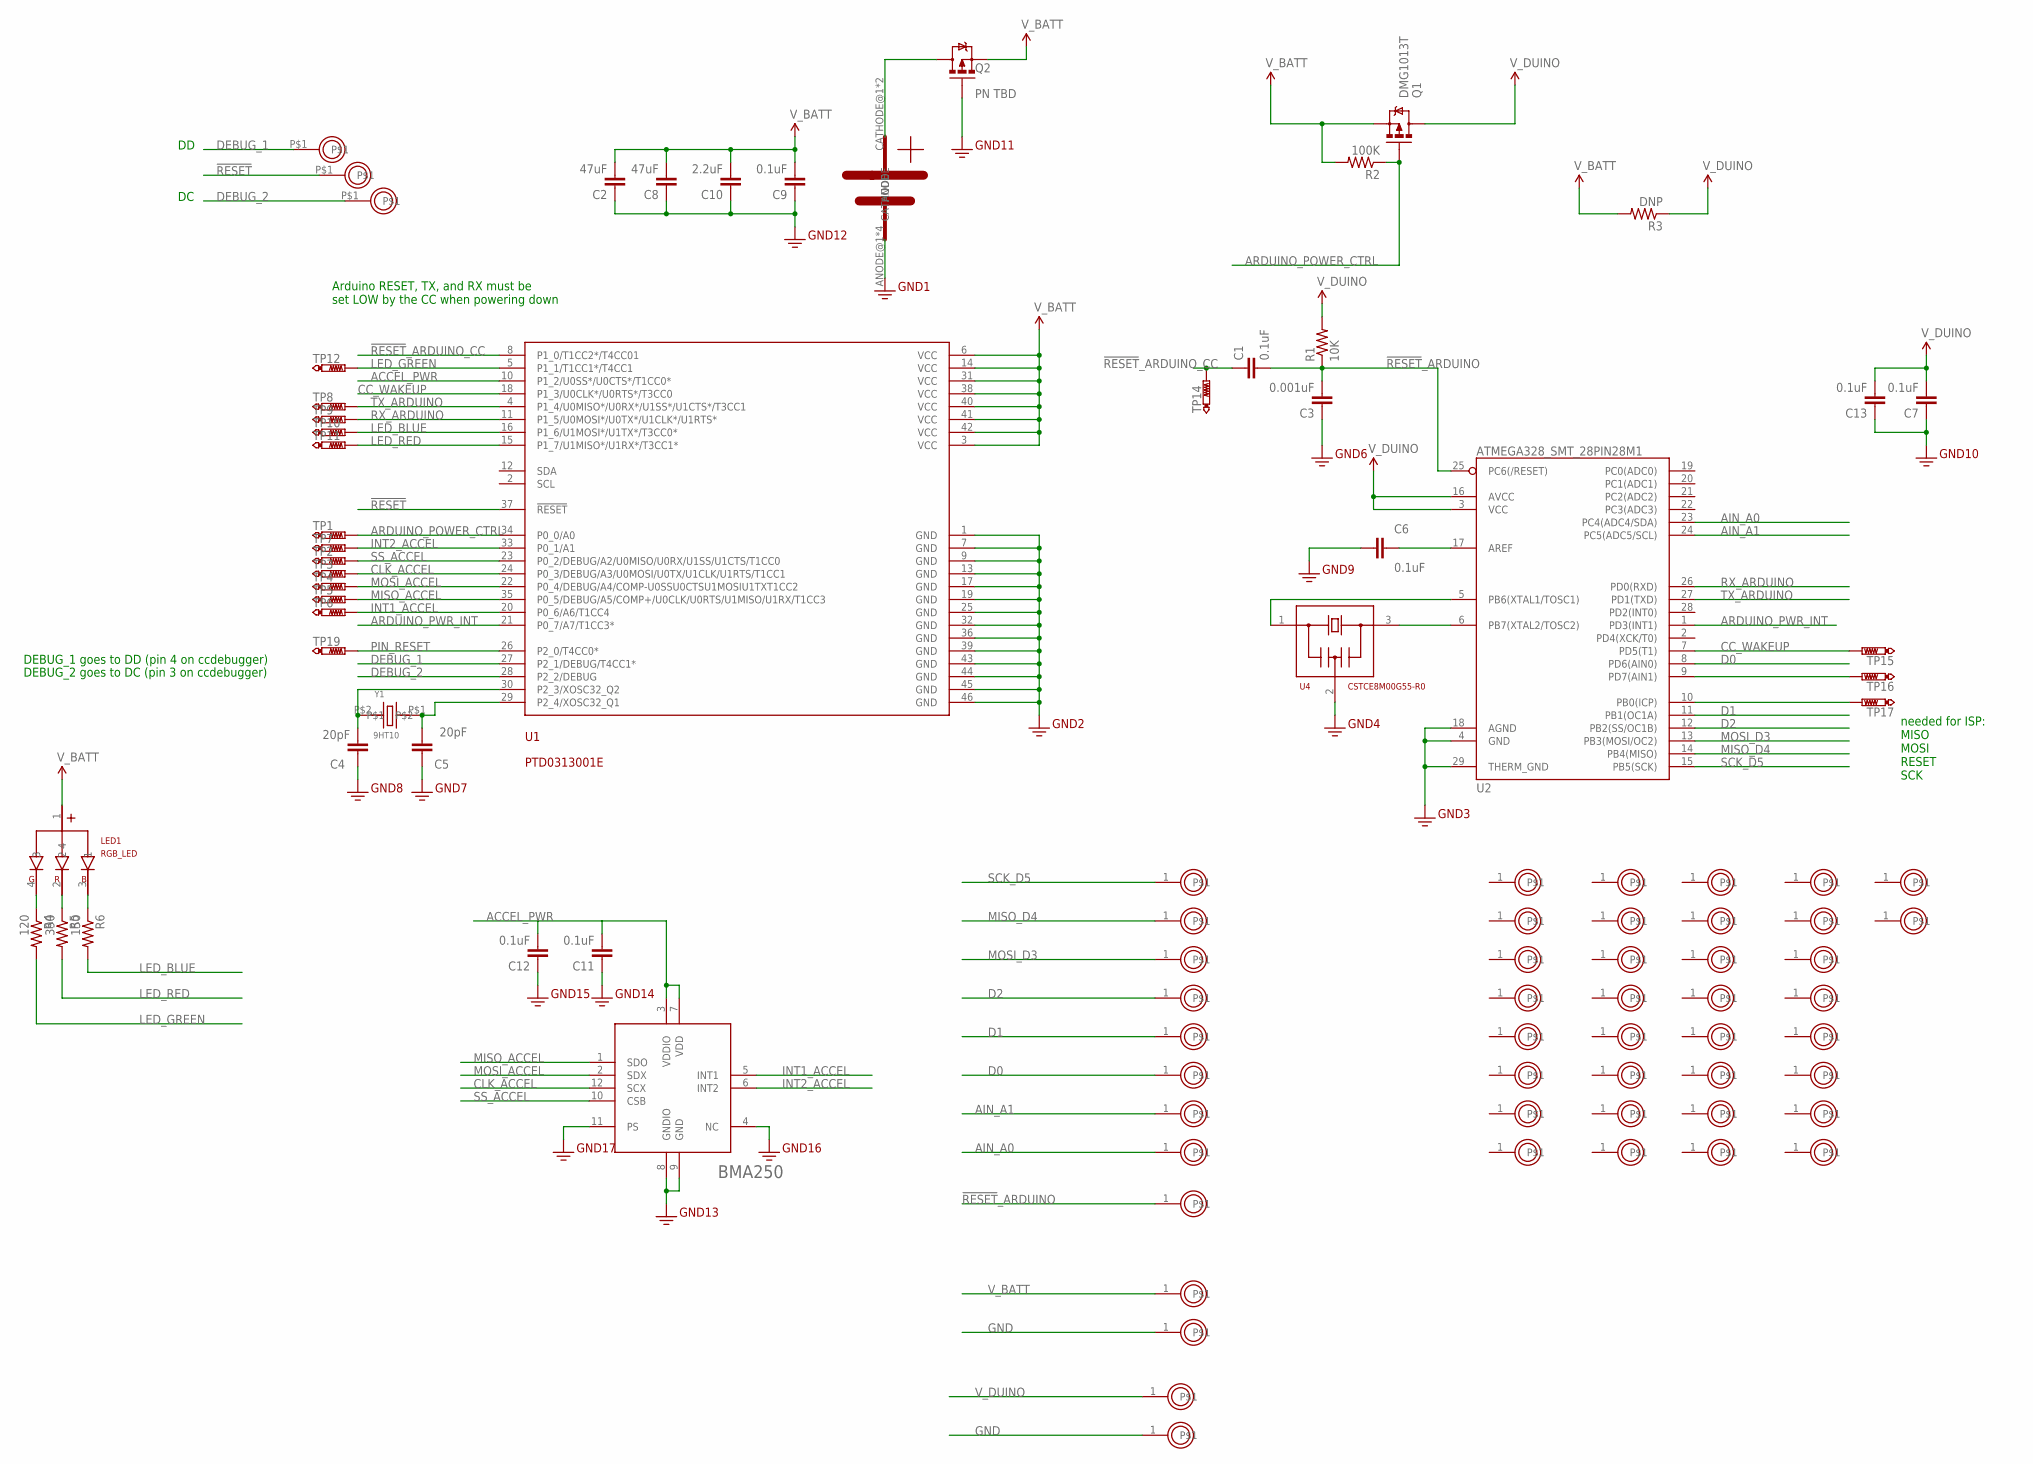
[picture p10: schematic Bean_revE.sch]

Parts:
C1, C6, C7, C9, C11, C12, C13: 0.1uF; 0402
C2, C8: 47uF; 0805
C3: 0.001uF; 0402
C4, C5: 20pF; 0402
C10: 2.2uF; 0603-CAP
CN_BATT: CR20324_ELEVATED_PADS; BK-912-ALT
LED1: RGB_LED; SML-LX0404SIUPGUSB
Q1: DMG1013T; SOT523
Q2: PN TBD; SOT523
R1: 10K; 0402
R2: 100K; 0402
R3: DNP; 0402
R4: 120; 0402
R5: 390; 0402
R6: 150; 0402
TP1, TP2, TP3, TP4, TP5, TP6, TP7, TP8, TP9, TP10, TP11, TP12, TP14, TP15, TP16, TP17: PTR1TP06R; TP06R
TP19: PTR1TP14R; TP14R
U1: PTD0313001E
U2: ATMEGA328_SMT_28PIN28M1; QFN-28-4X4
U3: BMA250
U4: CSTCE8M00G55-R0; CSTCE_G_3PIN_XTAL
U$1, U$3, U$4, U$5, U$6, U$7, U$8, U$9, U$10, U$11, U$12, U$13, U$14, U$15, U$16, U$17, U$18, U$19, U$20, U$21, U$22, U$23, U$24, U$25, U$26, U$27, U$28, U$29, U$30, U$31, U$32, U$33, U$34, U$35, U$36, U$37, U$38, U$39, U$40, U$41, U$42, U$43, U$44, U$45, U$46, U$52, U$53: PROTO_POINT; 1X01
U$49, U$50, U$51: BEAN_PROGRAM_PIN; BEAN_PROGAM_PIN
Y1: 9HT10

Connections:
!RESET!: U1.37 (!RESET!), U$50.P$1
!RESET!_ARDUINO: C1.P$2 (2), C3.P$2 (2), R1.P$1 (1), U2.25 (PC6(/RESET)), U$46.1
!RESET!_ARDUINO_CC: C1.P$1 (1), TP14.TP, U1.8 (P1_0/T1CC2*/T4CC01)
ACCEL_PWR: C11.P$2 (2), C12.P$2 (2), U1.10 (P1_2/U0SS*/U0CTS*/T1CC0*), U3.3 (VDDIO), U3.7 (VDD)
AIN_A0: U2.23 (PC4(ADC4/SDA)), U$10.1
AIN_A1: U2.24 (PC5(ADC5/SCL)), U$9.1
ARDUINO_POWER_CTRL: Q1.G, R2.P$1 (1), TP1.TP, U1.34 (P0_0/A0)
ARDUINO_PWR_INT: U1.21 (P0_7/A7/T1CC3*), U2.1 (PD3(INT1))
CC_WAKEUP: TP15.TP, U1.18 (P1_3/U0CLK*/U0RTS*/T3CC0), U2.7 (PD5(T1))
CLK_ACCEL: TP3.TP, U1.24 (P0_3/DEBUG/A3/U0MOSI/U0TX/U1CLK/U1RTS/T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), U3.12 (SCX)
D0: U2.8 (PD6(AIN0)), U$8.1
D1: U2.11 (PB1(OC1A)), U$7.1
D2: U2.12 (PB2(SS/OC1B)), U$6.1
DEBUG_1: U1.27 (P2_1/DEBUG/T4CC1*), U$51.P$1
DEBUG_2: U1.28 (P2_2/DEBUG), U$49.P$1
GND: C2.1, C3.P$1 (1), C4.P$1 (1), C5.P$1 (1), C6.P$1 (1), C7.P$1 (1), C8.1, C9.P$1 (1), C10.1, C11.P$1 (1), C12.P$1 (1), C13.P$1 (1), CN_BATT.ANODE@1 (ANODE), CN_BATT.ANODE@2 (ANODE), CN_BATT.ANODE@3 (ANODE), CN_BATT.ANODE@4 (ANODE), Q2.G, U1.1 (GND), U1.7 (GND), U1.9 (GND), U1.13 (GND), U1.17 (GND), U1.19 (GND), U1.25 (GND), U1.32 (GND), U1.36 (GND), U1.39 (GND), U1.43 (GND), U1.44 (GND), U1.45 (GND), U1.46 (GND), U2.4 (GND), U2.18 (AGND), U2.29 (THERM_GND), U3.4 (NC), U3.8 (GNDIO), U3.9 (GND), U3.11 (PS), U4.2, U$45.1, U$53.1
INT1_ACCEL: TP6.TP, U1.20 (P0_6/A6/T1CC4), U3.5 (INT1)
INT2_ACCEL: TP7.TP, U1.33 (P0_1/A1), U3.6 (INT2)
LED_BLUE: R6.P$2 (2), TP10.TP, U1.16 (P1_6/U1MOSI*/U1TX*/T3CC0*)
LED_GREEN: R4.P$2 (2), TP12.TP, U1.5 (P1_1/T1CC1*/T4CC1)
LED_RED: R5.P$2 (2), TP11.TP, U1.15 (P1_7/U1MISO*/U1RX*/T3CC1*)
MISO_ACCEL: TP5.TP, U1.35 (P0_5/DEBUG/A5/COMP+/U0CLK/U0RTS/U1MISO/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), U3.1 (SDO)
MISO_D4: U2.14 (PB4(MISO)), U$4.1
MOSI_ACCEL: TP4.TP, U1.22 (P0_4/DEBUG/A4/COMP-U0SSU0CTSU1MOSIU1TXT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), U3.2 (SDX)
MOSI_D3: U2.13 (PB3(MOSI/OC2)), U$5.1
unnamed: U2.5 (PB6(XTAL1/TOSC1)), U4.1
unnamed: U2.6 (PB7(XTAL2/TOSC2)), U4.3
unnamed: C4.P$2 (2), U1.30 (P2_3/XOSC32_Q2), Y1.P$2
unnamed: C5.P$2 (2), U1.29 (P2_4/XOSC32_Q1), Y1.P$1
unnamed: C6.P$2 (2), U2.17 (AREF)
unnamed: LED1.4 (3), R4.P$1 (1)
unnamed: LED1.2, R5.P$1 (1)
unnamed: LED1.3 (1), R6.P$1 (1)
PB0: TP17.TP, U2.10 (PB0(ICP))
PD7: TP16.TP, U2.9 (PD7(AIN1))
PIN_RESET: TP19.TP, U1.26 (P2_0/T4CC0*)
PRE_V_BATT: CN_BATT.CATHODE@1 (CATHODE), CN_BATT.CATHODE@2 (CATHODE), Q2.D
RX_ARDUINO: TP9.TP, U1.11 (P1_5/U0MOSI*/U0TX*/U1CLK*/U1RTS*), U2.26 (PD0(RXD))
SCK_D5: U2.15 (PB5(SCK)), U$3.1
SS_ACCEL: TP2.TP, U1.23 (P0_2/DEBUG/A2/U0MISO/U0RX/U1SS/U1CTS/T1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), U3.10 (CSB)
TX_ARDUINO: TP8.TP, U1.4 (P1_4/U0MISO*/U0RX*/U1SS*/U1CTS*/T3CC1), U2.27 (PD1(TXD))
V_BATT: C2.2, C8.2, C9.P$2 (2), C10.2, LED1.1 (4), Q1.S, Q2.S, R2.P$2 (2), R3.P$2 (2), U1.3 (VCC), U1.6 (VCC), U1.14 (VCC), U1.31 (VCC), U1.38 (VCC), U1.40 (VCC), U1.41 (VCC), U1.42 (VCC), U$52.1
V_DUINO: C7.P$2 (2), C13.P$2 (2), Q1.D, R1.P$2 (2), R3.P$1 (1), U2.3 (VCC), U2.16 (AVCC), U$1.1

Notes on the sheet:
needed for ISP: MISO MOSI RESET SCK
DEBUG_2 goes to DC (pin 3 on ccdebugger)
DEBUG_1 goes to DD (pin 4 on ccdebugger)
Arduino RESET, TX, and RX must be set LOW by the CC when powering down

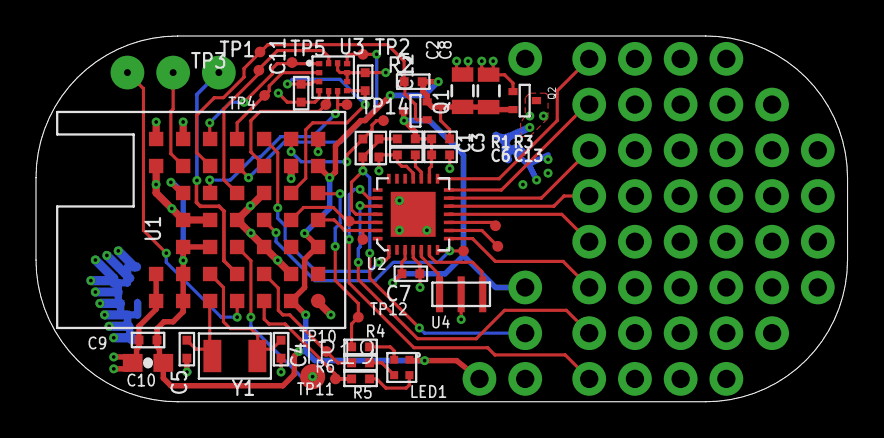
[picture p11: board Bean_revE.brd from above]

Board: 2 copper layers, 45.1 x 20.3 mm, 95 parts (1 on the bottom side), 43 nets.

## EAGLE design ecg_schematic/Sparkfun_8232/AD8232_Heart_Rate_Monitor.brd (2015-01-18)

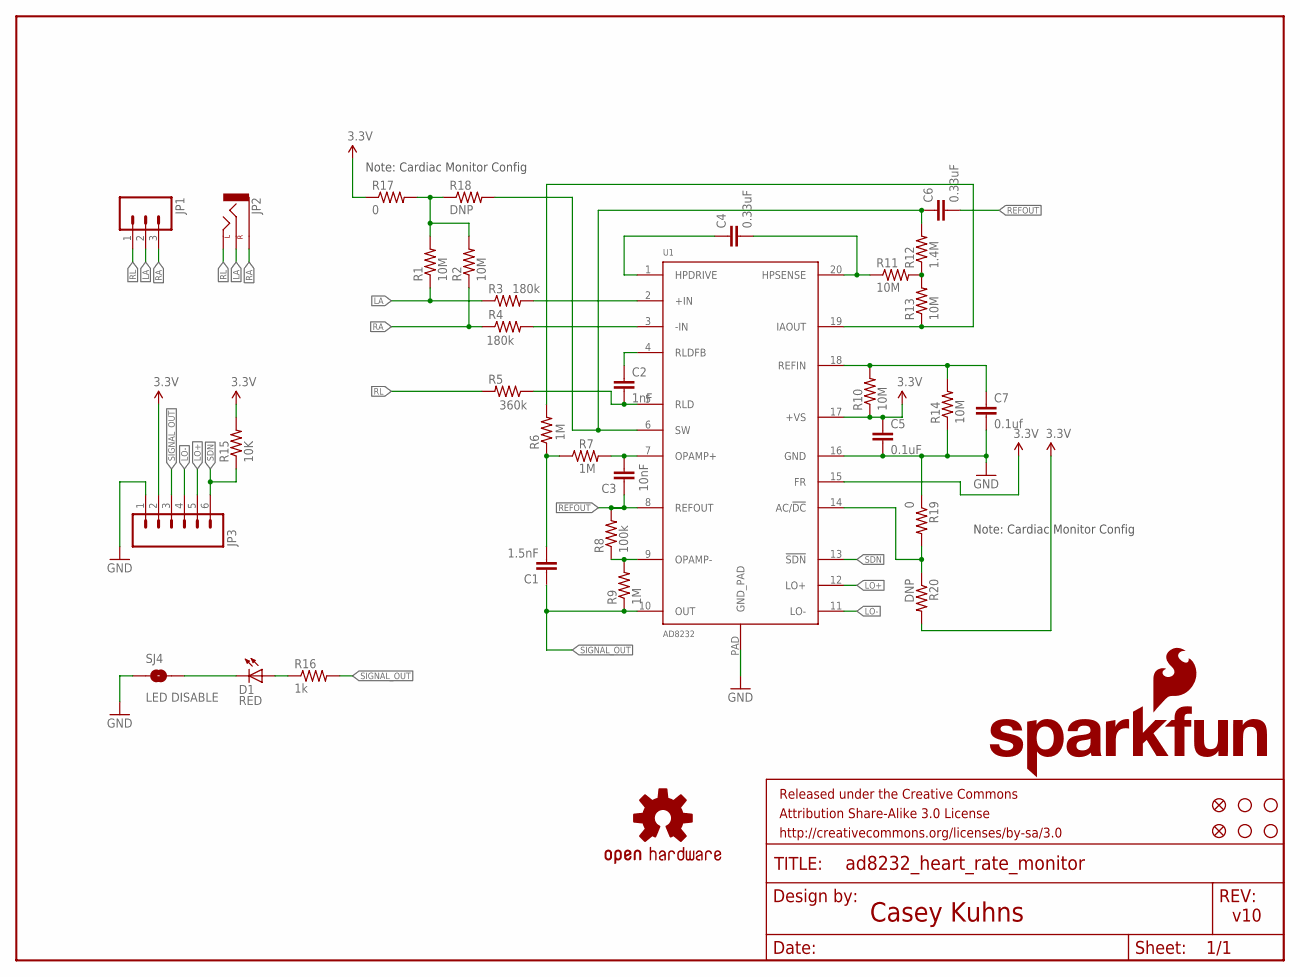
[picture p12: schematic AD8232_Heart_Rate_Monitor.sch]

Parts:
C1: 1.5nF; 0603-CAP
C2: 1nF; 0603-CAP
C3: 10nF; 0603-CAP
C4, C6: 0.33uF; 0805
C5: 0.1uF; 0603-CAP
C7: 0.1uf; 0603-CAP
D1: RED; LED-0603
FID1, FID2: FIDUCIAL1X2; FIDUCIAL-1X2
FRAME1: FRAME-LETTER; CREATIVE_COMMONS
JP1: M03PTH; 1X03
JP2: AUDIO-JACKSMD2; AUDIO-JACK-3.5MM-SMD
JP3: M06SIP; 1X06
LOGO1: OSHW-LOGOS; OSHW-LOGO-S
LOGO2: SFE_LOGO_NAME_FLAME.1_INCH; SFE_LOGO_NAME_FLAME_.1
R1, R2, R10, R11, R13, R14: 10M; 0603-RES
R3, R4: 180k; 0603-RES
R5: 360k; 0603-RES
R6, R7, R9: 1M; 0603-RES
R8: 100k; 0603-RES
R12: 1.4M; 0603-RES
R15: 10K; 0603-RES
R16: 1k; 0603-RES
R17, R19: 0; 0603
R18, R20: DNP; 0603
SJ4: LED DISABLE; SJ_2S-TRACE
STANDOFF1, STANDOFF2, STANDOFF3, STANDOFF4: STAND-OFF
U1: AD8232; LFCSP_20

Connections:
3.3V: C5.1, JP3.2, R10.1, R15.2, R17.1, R20.2, U1.15 (FR), U1.17 (+VS)
GND: C5.2, C7.2, JP3.1, R14.1, R19.1, SJ4.1, U1.16 (GND), U1.PAD (GND_PAD)
LA: JP1.2, JP2.RING (RIGHT), R1.1, R3.1
LO+: JP3.5, U1.12 (LO+)
LO-: JP3.4, U1.11 (LO-)
unnamed: R3.2, U1.2 (+IN)
unnamed: R4.2, U1.3 (-IN)
unnamed: C3.2, R7.2, U1.7 (OPAMP+)
unnamed: C4.2, R11.1, U1.20 (HPSENSE)
unnamed: C7.1, R10.2, R14.2, U1.18 (REFIN)
unnamed: D1.A, R16.1
unnamed: R8.1, R9.2, U1.9 (OPAMP-)
unnamed: R6.2, R13.1, U1.19 (IAOUT)
unnamed: C1.2, R6.1, R7.1
unnamed: D1.C, SJ4.2
unnamed: R19.2, R20.1, U1.14 (AC/!DC)
unnamed: C4.1, U1.1 (HPDRIVE)
unnamed: R11.2, R12.1, R13.2
unnamed: C6.1, R12.2, R18.2, U1.6 (SW)
unnamed: C2.1, U1.4 (RLDFB)
unnamed: C2.2, R5.1, U1.5 (RLD)
unnamed: R1.2, R2.2, R17.2, R18.1
RA: JP1.3, JP2.SLEEVE, R2.1, R4.1
REFOUT: C3.1, C6.2, R8.2, U1.8 (REFOUT)
RL: JP1.1, JP2.TIP (LEFT), R5.2
SDN: JP3.6, R15.1, U1.13 (!SDN)
SIGNAL_OUT: C1.1, JP3.3, R9.1, R16.2, U1.10 (OUT)

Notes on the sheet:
Casey Kuhns
v10
Note: Cardiac Monitor Config

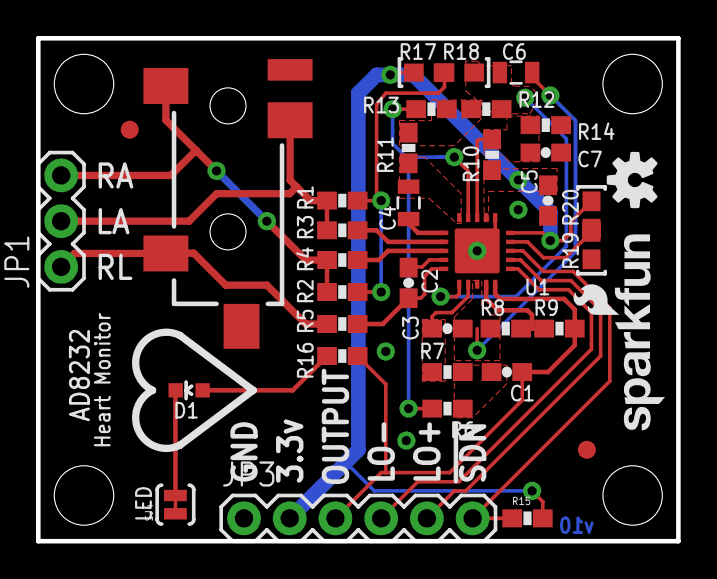
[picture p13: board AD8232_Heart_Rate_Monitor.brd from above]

Board: 2 copper layers, 35.6 x 27.9 mm, 42 parts (0 on the bottom side), 27 nets.

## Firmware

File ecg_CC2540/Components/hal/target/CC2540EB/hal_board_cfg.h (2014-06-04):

/*******************************************************************************
  Filename:       hal_board_cfg.h
  Revised:        $Date: 2013-09-12 11:31:38 -0700 (Thu, 12 Sep 2013) $
  Revision:       $Revision: 35293 $

  Description:

  Abstract board-specific registers, addresses, & initialization for H/W based on the
  Texas Instruments CC254x (8051 core).


  Copyright 2006-2013 Texas Instruments Incorporated. All rights reserved.

  IMPORTANT: Your use of this Software is limited to those specific rights
  granted under the terms of a software license agreement between the user
  who downloaded the software, his/her employer (which must be your employer)
  and Texas Instruments Incorporated (the "License").  You may not use this
  Software unless you agree to abide by the terms of the License. The License
  limits your use, and you acknowledge, that the Software may not be modified,
  copied or distributed unless embedded on a Texas Instruments microcontroller
  or used solely and exclusively in conjunction with a Texas Instruments radio
  frequency transceiver, which is integrated into your product.  Other than for
  the foregoing purpose, you may not use, reproduce, copy, prepare derivative
  works of, modify, distribute, perform, display or sell this Software and/or
  its documentation for any purpose.

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
  Should you have any questions regarding your right to use this Software,
  contact Texas Instruments Incorporated at www.TI.com.
*******************************************************************************/
#ifndef HAL_BOARD_CFG_H
#define HAL_BOARD_CFG_H

#ifdef __cplusplus
extern "C"
{
#endif


/*******************************************************************************
 * INCLUDES
 */

#include "hal_mcu.h"
#include "hal_defs.h"
#include "hal_types.h"

/*******************************************************************************
 * CONSTANTS
 */

/* Board Identifier */

#if !defined (HAL_BOARD_CC2530EB_REV17) && !defined (HAL_BOARD_CC2530EB_REV13)
  #define HAL_BOARD_CC2530EB_REV17
#endif

/* Clock Speed */

#define HAL_CPU_CLOCK_MHZ             32

/* Sleep Clock */

#define EXTERNAL_CRYSTAL_OSC          0x00  // external 32kHz XOSC
#define INTERNAL_RC_OSC               0x80  // internal 32kHz RCOSC

// For non-USB, assume external, unless an internal crystal is explicitly indicated.
#if !defined (XOSC32K_INSTALLED) || (defined (XOSC32K_INSTALLED) && (XOSC32K_INSTALLED == TRUE))
#define OSC_32KHZ                     EXTERNAL_CRYSTAL_OSC
#else
#define OSC_32KHZ                     INTERNAL_RC_OSC
#endif

// Minimum Time for Stable External 32kHz Clock (in ms)
#define MIN_TIME_TO_STABLE_32KHZ_XOSC 400

/* LCD Max Chars and Buffer */
#define HAL_LCD_MAX_CHARS   16
#define HAL_LCD_MAX_BUFF    25

/* LED Configuration */

#if defined (HAL_BOARD_CC2530EB_REV17) && !defined (HAL_PA_LNA) && !defined (HAL_PA_LNA_CC2590)
  #define HAL_NUM_LEDS                 3
#elif defined (HAL_BOARD_CC2530EB_REV13) || defined (HAL_PA_LNA) || defined (HAL_PA_LNA_CC2590)
  #define HAL_NUM_LEDS                 1
#else
  #error Unknown Board Indentifier
#endif

#define HAL_LED_BLINK_DELAY()   st( { volatile uint32 i; for (i=0; i<0x5800; i++) { }; } )

/* 1 - Green */
#define LED1_BV                        BV(0)
#define LED1_SBIT                      P1_0
#define LED1_DDR                       P1DIR
#define LED1_POLARITY                  ACTIVE_HIGH

#ifdef HAL_BOARD_CC2530EB_REV17
  /* 2 - Red */
  #define LED2_BV                      BV(1)
  #define LED2_SBIT                    P1_1
  #define LED2_DDR                     P1DIR
  #define LED2_POLARITY                ACTIVE_HIGH

  /* 3 - Yellow */
  #define LED3_BV                      BV(4)
  #define LED3_SBIT                    P1_4
  #define LED3_DDR                     P1DIR
  #define LED3_POLARITY                ACTIVE_HIGH
#endif

/* Push Button Configuration */

#define ACTIVE_LOW                     !
#define ACTIVE_HIGH                    !!    /* double negation forces result to be '1' */

/* S1 */
#define PUSH1_BV                       BV(1)
#define PUSH1_SBIT                     P0_1

#ifdef HAL_BOARD_CC2530EB_REV17
  #define PUSH1_POLARITY               ACTIVE_HIGH
#elif defined (HAL_BOARD_CC2530EB_REV13)
  #define PUSH1_POLARITY               ACTIVE_LOW
#else
  #error Unknown Board Indentifier
#endif

/* Joystick Center Press */
#define PUSH2_BV                       BV(0)
#define PUSH2_SBIT                     P2_0
#define PUSH2_POLARITY                 ACTIVE_HIGH

/* OSAL NV implemented by internal flash pages. */

// Flash is partitioned into 8 banks of 32 KB or 16 pages.
#define HAL_FLASH_PAGE_PER_BANK        16

// Flash is constructed of 128 pages of 2 KB.
#define HAL_FLASH_PAGE_PHYS            2048

// SNV can use a larger logical page size to accomodate more or bigger items or extend lifetime.
#define HAL_FLASH_PAGE_SIZE            HAL_FLASH_PAGE_PHYS
#define HAL_FLASH_WORD_SIZE            4

// CODE banks get mapped into the XDATA range 8000-FFFF.
#define HAL_FLASH_PAGE_MAP             0x8000

// The last 16 bytes of the last available page are reserved for flash lock bits.
#define HAL_FLASH_LOCK_BITS            16

// NV page definitions must coincide with segment declaration in project *.xcl file.
#if defined NON_BANKED
#define HAL_NV_PAGE_END                30
#elif defined HAL_BOARD_CC2541S
#define HAL_NV_PAGE_END                125
#elif defined HAL_BOARD_F128
#define HAL_NV_PAGE_END                62
#else
#define HAL_NV_PAGE_END                126
#endif

// Re-defining Z_EXTADDR_LEN here so as not to include a Z-Stack .h file.
#define HAL_FLASH_IEEE_SIZE            8
#define HAL_FLASH_IEEE_PAGE            (HAL_NV_PAGE_END+1)
#define HAL_FLASH_IEEE_OSET            (HAL_FLASH_PAGE_SIZE - HAL_FLASH_LOCK_BITS - HAL_FLASH_IEEE_SIZE)
#define HAL_INFOP_IEEE_OSET            0xC

#define HAL_NV_PAGE_CNT                2
#define HAL_NV_PAGE_BEG                (HAL_NV_PAGE_END-HAL_NV_PAGE_CNT+1)

// Used by DMA macros to shift 1 to create a mask for DMA registers.
#define HAL_NV_DMA_CH                  0
#define HAL_DMA_CH_RX                  3
#define HAL_DMA_CH_TX                  4

#define HAL_NV_DMA_GET_DESC()  HAL_DMA_GET_DESC0()
#define HAL_NV_DMA_SET_ADDR(a) HAL_DMA_SET_ADDR_DESC0((a))

/* Critical Vdd Monitoring to prevent flash damage or radio lockup. */

// Vdd/3 / Internal Reference X ENOB --> (Vdd / 3) / 1.15 X 127
#define VDD_2_0  74   // 2.0 V required to safely read/write internal flash.
#define VDD_2_7  100  // 2.7 V required for the Numonyx device.

#define VDD_MIN_RUN   VDD_2_0
#define VDD_MIN_NV   (VDD_2_0+4)  // 5% margin over minimum to survive a page erase and compaction.
#define VDD_MIN_XNV  (VDD_2_7+5)  // 5% margin over minimum to survive a page erase and compaction.

/*******************************************************************************
 * MACROS
 */

/* Cache Prefetch Control */

#define PREFETCH_ENABLE()  st( FCTL = 0x08; )
#define PREFETCH_DISABLE() st( FCTL = 0x04; )

/* Setting Clocks */

// switch to the 16MHz HSOSC and wait until it is stable
#define SET_OSC_TO_HSOSC()                                                     \
{                                                                              \
  CLKCONCMD = (CLKCONCMD & 0x80) | CLKCONCMD_16MHZ;                            \
  while ( (CLKCONSTA & ~0x80) != CLKCONCMD_16MHZ );                            \
}

// switch to the 32MHz XOSC and wait until it is stable
#define SET_OSC_TO_XOSC()                                                      \
{                                                                              \
  CLKCONCMD = (CLKCONCMD & 0x80) | CLKCONCMD_32MHZ;                            \
  while ( (CLKCONSTA & ~0x80) != CLKCONCMD_32MHZ );                            \
}

// set 32kHz OSC and wait until it is stable
#define SET_32KHZ_OSC()                                                        \
{                                                                              \
  CLKCONCMD = (CLKCONCMD & ~0x80) | OSC_32KHZ;                                 \
  while ( (CLKCONSTA & 0x80) != OSC_32KHZ );                                   \
}

#define START_HSOSC_XOSC()                                                     \
{                                                                              \
  SLEEPCMD &= ~OSC_PD;            /* start 16MHz RCOSC & 32MHz XOSC */         \
  while (!(SLEEPSTA & XOSC_STB)); /* wait for stable 32MHz XOSC */             \
}

#define STOP_HSOSC()                                                           \
{                                                                              \
  SLEEPCMD |= OSC_PD;             /* stop 16MHz RCOSC */                       \
}

/* Board Initialization */
#define HAL_BOARD_INIT()                                                       \
{                                                                              \
  /* Set to 16Mhz to set 32kHz OSC, then back to 32MHz */                      \
  START_HSOSC_XOSC();                                                          \
  SET_OSC_TO_HSOSC();                                                          \
  SET_32KHZ_OSC();                                                             \
  SET_OSC_TO_XOSC();                                                           \
  STOP_HSOSC();                                                                \
                                                                               \
  /* Enable cache prefetch mode. */                                            \
  PREFETCH_ENABLE();                                                           \
}

/* Debounce */
#define HAL_DEBOUNCE(expr)    { int i; for (i=0; i<500; i++) { if (!(expr)) i = 0; } }

/* ----------- Push Buttons ---------- */
#define HAL_PUSH_BUTTON1()        (PUSH1_POLARITY (PUSH1_SBIT))
#define HAL_PUSH_BUTTON2()        (PUSH2_POLARITY (PUSH2_SBIT))
#define HAL_PUSH_BUTTON3()        (0)
#define HAL_PUSH_BUTTON4()        (0)
#define HAL_PUSH_BUTTON5()        (0)
#define HAL_PUSH_BUTTON6()        (0)

/* LED's */

#if defined (HAL_BOARD_CC2530EB_REV17) && !defined (HAL_PA_LNA) && !defined (HAL_PA_LNA_CC2590)

  #define HAL_TURN_OFF_LED1()       st( LED1_SBIT = LED1_POLARITY (0); )
  #define HAL_TURN_OFF_LED2()       st( LED2_SBIT = LED2_POLARITY (0); )
  #define HAL_TURN_OFF_LED3()       st( LED3_SBIT = LED3_POLARITY (0); )
  #define HAL_TURN_OFF_LED4()       HAL_TURN_OFF_LED1()

  #define HAL_TURN_ON_LED1()        st( LED1_SBIT = LED1_POLARITY (1); )
  #define HAL_TURN_ON_LED2()        st( LED2_SBIT = LED2_POLARITY (1); )
  #define HAL_TURN_ON_LED3()        st( LED3_SBIT = LED3_POLARITY (1); )
  #define HAL_TURN_ON_LED4()        HAL_TURN_ON_LED1()

  #define HAL_TOGGLE_LED1()         st( if (LED1_SBIT) { LED1_SBIT = 0; } else { LED1_SBIT = 1;} )
  #define HAL_TOGGLE_LED2()         st( if (LED2_SBIT) { LED2_SBIT = 0; } else { LED2_SBIT = 1;} )
  #define HAL_TOGGLE_LED3()         st( if (LED3_SBIT) { LED3_SBIT = 0; } else { LED3_SBIT = 1;} )
  #define HAL_TOGGLE_LED4()         HAL_TOGGLE_LED1()

  #define HAL_STATE_LED1()          (LED1_POLARITY (LED1_SBIT))
  #define HAL_STATE_LED2()          (LED2_POLARITY (LED2_SBIT))
  #define HAL_STATE_LED3()          (LED3_POLARITY (LED3_SBIT))
  #define HAL_STATE_LED4()          HAL_STATE_LED1()
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

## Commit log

2014-03-05 Visualizer with square wave from Arduino
2014-04-03 Trying 50 Hz notch filter
2014-04-08 MIT-BIH ECG data for simulation
    [mit_bih_100.csv, mit_bih_101.csv, mit_bih_111.csv, mit_bih_228.csv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]
2014-04-09 Synthesized ecg data
    [synth1_512samp_per_sec.csv]
2014-05-01 Fixed bug. Martens' PLL without error filtering and adaptation suppression works
2014-05-02 Bug fix: Error filter cutoff freq
2014-05-12 minor re-organization
    [mit_bih_100.csv, mit_bih_101.csv, mit_bih_111.csv, mit_bih_228.csv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]
2014-05-12 Real recordings
    [data0_G_500_chest.csv, data1_G_500_chest.csv, data2_G_500_chest.csv, data3_G_60_chest.csv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]
2014-05-13 one more data point
    [data5_G_60_chest.csv]
2014-05-13 Another data point
    [data6_G_60_chest.csv]
2014-05-15 Data from Faraday cage in GB's lab
    [ecg_plot_17.csv, ecg_plot_18.csv, ecg_plot_19.csv, ecg_plot_20.csv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]
2014-05-16 Added ADC resolution and sample rate
2014-05-16 Data for custom 3 electrode (dry) board
    [ecg_plot_0.csv, ecg_plot_1.csv, ecg_plot_10.csv, ecg_plot_2.csv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]
2014-05-16 psuedo 2 electrode
    [ecg_plot_0.csv, ecg_plot_1.csv, ecg_plot_2.csv, ecg_plot_3.csv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]
2014-05-16 Adaptive filter screenshots
2014-05-16 Filtering psuedo 2-electrode data
2014-05-19 Data for single ended electrode
    [ecg_plot_0.csv, ecg_plot_1.csv, ecg_plot_2.csv, ecg_plot_3.csv]
2014-05-19 input set to single ended 2 electrode config
2014-05-19 Screenshots of adaptive filtering in action
2014-05-19 One more screenshot of adaptive filtering in action
2014-05-19 2 electrode diff. with entire circuit and laptop on my lap
    [ecg_plot_0.csv, ecg_plot_1.csv]
2014-05-19 One more data point with lappy on lap
    [ecg_plot_0.csv]
2014-05-19 adaptive filtering on diff. amp with lappy on lap
2014-05-20 Psuedo 2-electrode with RLD
    [ecg_plot_2.csv, ecg_plot_3.csv, ecg_plot_4.csv, ecg_plot_5.csv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]
2014-05-25 Renamed project
    [data0_G_500_chest.csv, data1_G_500_chest.csv, data2_G_500_chest.csv, data3_G_60_chest.csv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]
2014-05-31 Arduino schematic added
2014-06-05 Data from BLE based pseudo-2-RLD ECG
    [ecg_plot_0.csv, ecg_plot_1.csv]
2014-06-06 CR2032 battery test
2014-06-09 Single battery CR2032 with REF3320
    [ecg_plot_1.csv]
2014-06-11 Initial long term recordings
    [long_reading1402474121895.csv]
2014-06-11 More data from belt
    [long_reading1402480585442.csv, long_reading1402481074924.csv, long_reading1402481332299.csv, long_reading1402486000596.csv]
2014-06-26 data with LP5907
    [ecg_plot_1.csv]
2014-06-27 Passive dry ground with belt
    [ecg_plot_0.csv, ecg_plot_1.csv, ecg_plot_2.csv]
2014-06-30 mentioned hi-z when talking about pseudo 2-electrodes
2014-07-24 CR2032 BLE with PDMS layer
    [ecg_plot_0.csv, ecg_plot_1.csv, ecg_plot_2.csv]
2014-08-29 Haynes test done
    [short_reading.csv]
2014-11-25 intial commit
    [AD8232_Heart_Rate_Monitor.brd, AD8232_Heart_Rate_Monitor.sch, BOM_NBMC_LBM313.xlsx, Bean_revE.brd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]
2014-11-25 added testpoints ,100uf cap, cap across thermistor,JP2,removed battery and battery holder connection proper
    [NBMC_SCHEMATIC_with_LBM313.sch]
2014-11-26 updated BOM with the new changes of TP,100uF cap etc
    [BOM_NBMC_LBM313.xlsx, NBMC_SCHEMATIC_with_LBM313.sch, NBMC_SCHEMATIC_with_LBM313_partlist.csv]
2014-12-05 reset filter is added, Thermistor removed and the testpoint connections to the JP1 are removed
    [BOM_NBMC_LBM313.xlsx, NBMC_SCHEMATIC_with_LBM313.sch]
2014-12-18 mouser BOM added and ordered
    [BOM_NBMC_LBM313.xlsx, NBMC_SCHEMATIC_with_LBM313.sch, partlist.csv]
2015-01-18 Moved ecg_schematic under ZZZ
    [AD8232_Heart_Rate_Monitor.brd, AD8232_Heart_Rate_Monitor.sch, BOM_NBMC_LBM313.xlsx, Bean_revE.brd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]
2015-01-18 Merging of ecg_schematic complete
    Schematic files moved under the same repository and all unused data is
    removed
    [AD8232_Heart_Rate_Monitor.brd, AD8232_Heart_Rate_Monitor.sch, BOM_NBMC_LBM313.xlsx, Bean_revE.brd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]

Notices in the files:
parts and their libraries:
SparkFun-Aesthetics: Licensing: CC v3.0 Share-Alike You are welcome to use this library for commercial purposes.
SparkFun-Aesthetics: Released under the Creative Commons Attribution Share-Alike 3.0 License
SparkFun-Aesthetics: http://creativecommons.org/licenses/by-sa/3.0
